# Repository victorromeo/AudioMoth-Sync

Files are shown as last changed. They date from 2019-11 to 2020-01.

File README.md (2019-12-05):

# AudioMoth-Sync

## DESCRIPTION

This project supports the Monash University AgTech Rodent Tracking project, to detect animal activity and trigger recording devices to acquire ultrasonic audio samples and photogrphic evidence required to document the animal activity and identify the related animal species.

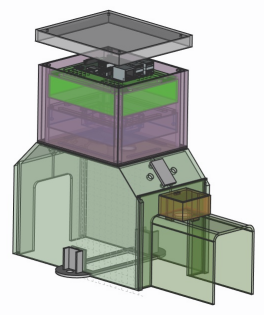
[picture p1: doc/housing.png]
Housing
<br>
*Original concept of the rodent detection housing*

## CONCEPT

An AudioMoth unit has a Cortex M4 EFM32WG380F256 MCU which is capable of supporting USB access as well as recording audio.
*(The two operations cannot occur at the same time however, as the processors internal capacity to handle the audio buffers and switch SD card access is insufficent)*

Instead, an AudioMoth is connected via USB to a Raspberry PI, and GPIO pins.  The Raspberry PI has PIR senses which detect the infrared emitted from animals.  

When an animal is detected, the Raspberry PI signals to the AudioMoth over GPIO to commence recording, and access to the AudioMoth sound recordings is removed.  In addition to the microphone activity, the Raspberry PI begins taking photos of animals inside the housing.  

When motion stops, after a delay the Raspberry PI signals to the AudioMoth to stop recording.  The AudioMoth enables the Mass Storage Device features on the MCU and the Raspberry PI detects the AudioMoth filesystem and mounts it.  Files are then transferred locally onto a microSD Card used by the Raspberry PI.  Once files are transferred, the recordings are removed from the AudioMoth microSD card, using remote access operations on the mounted filesystem.

A seperate background task, which is always running sends the sound and photo files into the cloud via a WiFi // 4G connection which is available.  Once the files are transmitted successfully to the cloud, the locally stored files are removed from the local device.

## PREREQUISITES

- Raspberry PI ([3B+](https://www.raspberrypi.org/products/raspberry-pi-3-model-b-plus/) or [4B](https://www.raspberrypi.org/products/raspberry-pi-4-model-b/))
    - 16GB or 32GB SD microSD card (For the OS)
    - [Raspbian](https://www.raspberrypi.org/downloads/raspbian/)
    - Power Supply
        - [2.5mA microUSB for RPi 3B+](https://www.raspberrypi.org/products/raspberry-pi-universal-power-supply/)
        - [15W Type-C for RPi 4B](https://www.raspberrypi.org/products/type-c-power-supply/)
        - Battery pack
        - 20W Solar panel and solar controller with load controller and external battery supply with USB support
        - PiJuice with LIPO battery and 20W Solar Panel
    - [RTC for Rpi](https://core-electronics.com.au/ds1307-rtc-module-with-battery-for-raspberry-pi.html)
    - [Duinotech XC9021 5MP Night Vision camera for Raspberry PI](https://www.jaycar.com.au/5mp-night-vision-camera-for-raspberry-pi/p/XC9021)
- AudioMoth (1.0.0 or later)
    - 16GB or 32GB SD microSD card (For the Audio samples)
    - [AudioMoth-MSD firmware](https://github.com/victorromeo/AudioMoth-MSD)
    - 2.54 right angle header 6 pin [female](https://core-electronics.com.au/0-100-2-54-mm-female-header-1x6-pin-right-angle.html) or [male](https://core-electronics.com.au/0-100-2-54-mm-breakaway-male-header-1x40-pin-right-angle.html)
    - [Dupont wires](https://www.altronics.com.au/p/p1017-prototyping-jumper-wires-mixed-for-breadboard-arduino/)
    - [Duinotech Raspberry Pi GPIO Expansion Shield](https://www.jaycar.com.au/duinotech-raspberry-pi-gpio-expansion-shield-with-4-x-ad-da/p/XC9050)
    - AA batteries to provide additional current requirements
- Housing
    - FreeCAD files
    - [Duinotech XC-4444 PIR Infrared Motion Sensor](https://core-electronics.com.au/modmypi-pir-infrared-motion-sensor-hc-sr501.html)
- Construction
    - Hot Glue gun
    - Soldering iron and Solder, used to mount the 6 pin header on the AudioMoth
    - 3D Printer (220 x 220 x 250 print bed), e.g. Ender 3
    - Silicon sealant

## RASPBERRY PI SETUP

### Setup of the Camera

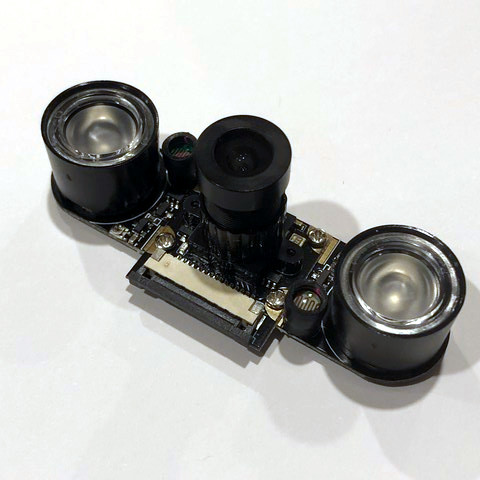
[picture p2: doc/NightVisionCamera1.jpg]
Camera


1. Run Raspi-Config to enable camera interface
    - `sudo raspi-config` ... `Interface Options` ... `Enable Camera` ... `Finish`
2. Power off the Raspberry PI
3. Plug in the 5 MP Nightvision camera
4. Power on the Raspberry PI
5. Execute `raspistill -o test.jpg` to validate that the camera is working, a file with the name test.jpg should appear in the current folder. If a screen is connected, view the image to validate that the photo is in focus.  If no screen is attached to the raspberry pi, use file transfer to view the image.

### Setup of the Realtime Clock

1. Run Raspi-Config to enable the I2C interface
    - `sudo raspi-config` ... `Interface Options` ... `Advanced Options` ... `I2C` .. `Finish`
2. Power off the Raspberry PI
3. Connect the RTC unit over pins 1-10 of the Raspberry PI
4. Power on the Raspberry PI
5. In a terminal window check to ensure the RTC chip is detected
    - `sudo i2cdetect -y 1` ... 68, which is the RTC hexidecimal I2C address of the device should appear
6. Load the RTC module
    - `sudo modprobe rtc-ds1307`
7. Register the device
    - `sudo echo ds1307 0x68 > /sys/class/i2c-adapter/i2c-1/new_device`
8. Read the time from the RTC
    - `sudo hwclock -r`
9. If the Raspberry PI device is connected to the internet via WiFi or Ethernet, check the time
    - `date`
10. Write the time to the RTC
    - `sudo hwclock -w`
11. Add the RTC clock to the Raspberry PI modules list
    - `sudo nano /etc/modules` and add `rtc-ds1307` at the end of the file. Save (Control + o) and exit (Control + x, y).
12. Add the RTC clock to the boot script
    - `sudo nano /etc/rc.local` and add the following.

    ```
    echo ds1307 0x68 > /sys/class/i2c-adapter/i2c-1/new_device
    sudo hwclock -s
    date
    ```
    Save (Control + o) and exit (Control + x, y).
13. Disconnect the network and check that time is still accessible
    - `date`

### Setup Python 3

1. Update the list of available packages
    - `sudo apt update`
2. Upgrade the currently installed packages
    - `sudo apt upgrade`
3. Install the picamera component
    - `sudo apt install python3-picamera`

### Setup Sync Scripts

1. Change to home directory of
    - `cd ~`
2. Clone the scripts into the root directory
    - `git clone https://github.com/victorromeo/AudioMoth-Sync.git`

### Setup Cron Job

1. Change to the directory of the AudioMoth-Sync
    - `cd ~/AudioMoth-Sync`
2. Update exec permission on the launcher script
    - `chmod 755 launcher.sh`
3. Test that the script executes
    - `sh launcher.sh`
4. Add launcher.sh to crontab
    - `sudo crontab -e` and add the following to the end of the file
    - `@reboot sh /home/pi/AudioMoth-Sync/launcher.sh > /home/pi/AudioMoth-Sync/logs/cronlog 2>&1`
5. Power off the Raspberry PI
6. Power on the Raspberry PI
7. Troubleshoot by inspecting the logs
    - `cat /home/pi/AudioMoth-Sync/logs/cronlog`

## AUDIOMOTH SETUP

### Flash the firmware

1. Download the firmware from AudioMoth-MSD
2. Connect the AudioMoth to a PC a USB cable
3. [Flash](https://github.com/OpenAcousticDevices/Flash) the device, using the AudioMoth-Project.bin file and instructions on the flash project.  Briefly this can be explained as follows
    - Connect pins 1 and 3 together, (pulling the SWCLK to VCC)
    - Change the switch to the Custom setting on the AudioMoth
    - `flash -i /dev/ttyACM0` or similar, to get the serial number
    - `flash -u /dev/ttyACM0 AudioMoth-Project.bin` (execute several times as needed to get the firmware to upload onto the device)

### Connectors

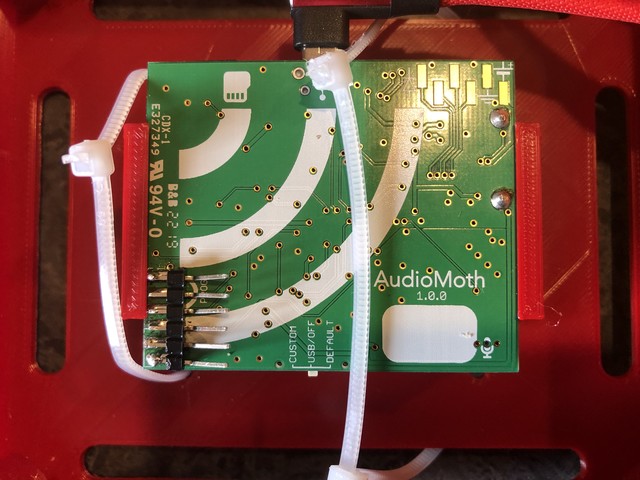
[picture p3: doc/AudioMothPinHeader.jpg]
AudioMoth Headers


1. Solder the 2.54 right angle header 6 pins onto the AudioMoth
2. Connect Dupont connectors onto the pins, exposing female connectors on the opposite end available to connect onto the Raspberry PI

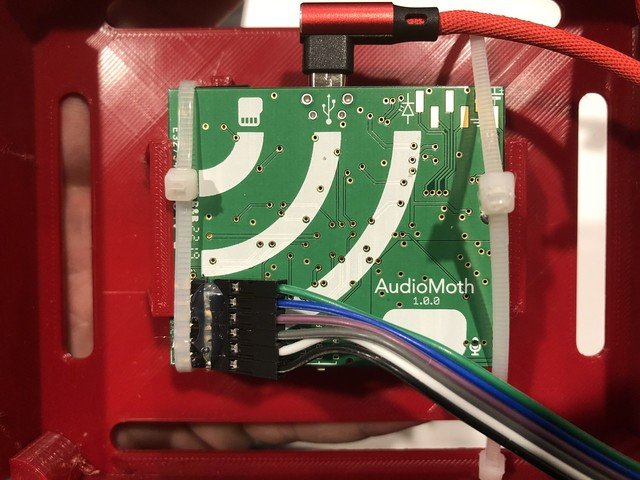
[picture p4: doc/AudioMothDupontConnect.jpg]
AudioMoth Header Connections


## CONSTRUCTION

### 3D Print the housing 

You will require
- 1 x Lid
- 1 x Electronics Unit
- 1 x Electronics Base
- 1 x AudioMoth Holder
- 1 x Raspberry PI Holder
- 2 x Trap Sides
- 2 x Trap Brackets
- 2 x Tunnels
- 2 x PIR Cover
- 1 x Peg Bracket

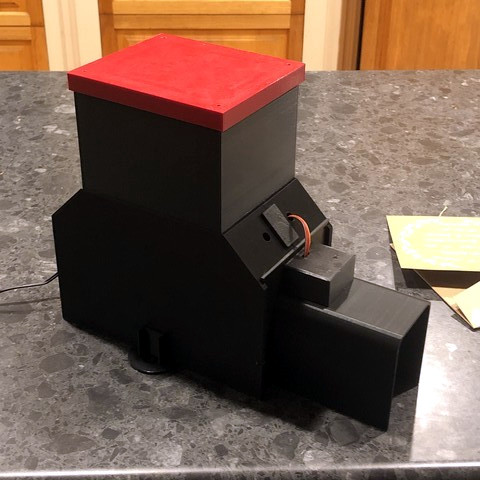
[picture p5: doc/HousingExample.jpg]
Housing Example
<br>
*Housing*

### PIR Installation

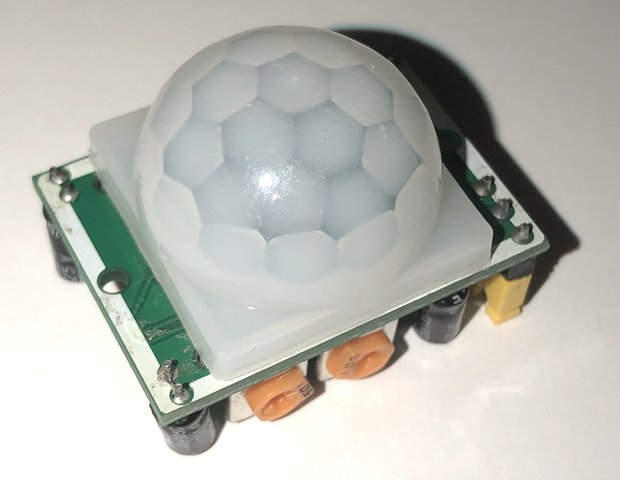
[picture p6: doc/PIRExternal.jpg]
PIR


1. Sit the PIR unit in the hole in top of the Tunnel, white dome facing downward, and secure with Hot Glue to prevent movement.

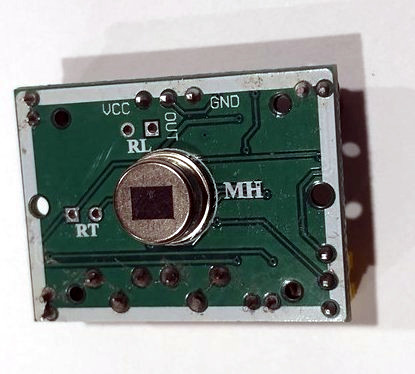
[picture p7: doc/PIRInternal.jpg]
PIR Internal


2. Connect Dupont cables to the 3 header pins point upward.
The pins are VCC (5 Volt), OUT (3.3V Max), GND

3. Tune the PIR sensitivity as required.  Default settings should be adequate. 

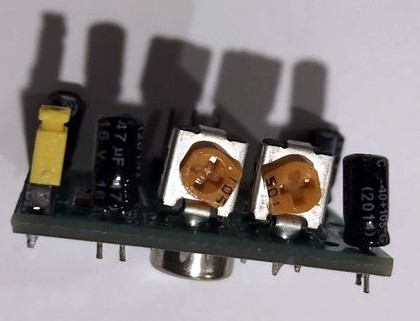
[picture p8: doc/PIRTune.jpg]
PIR Tune


### Wiring GPIO 

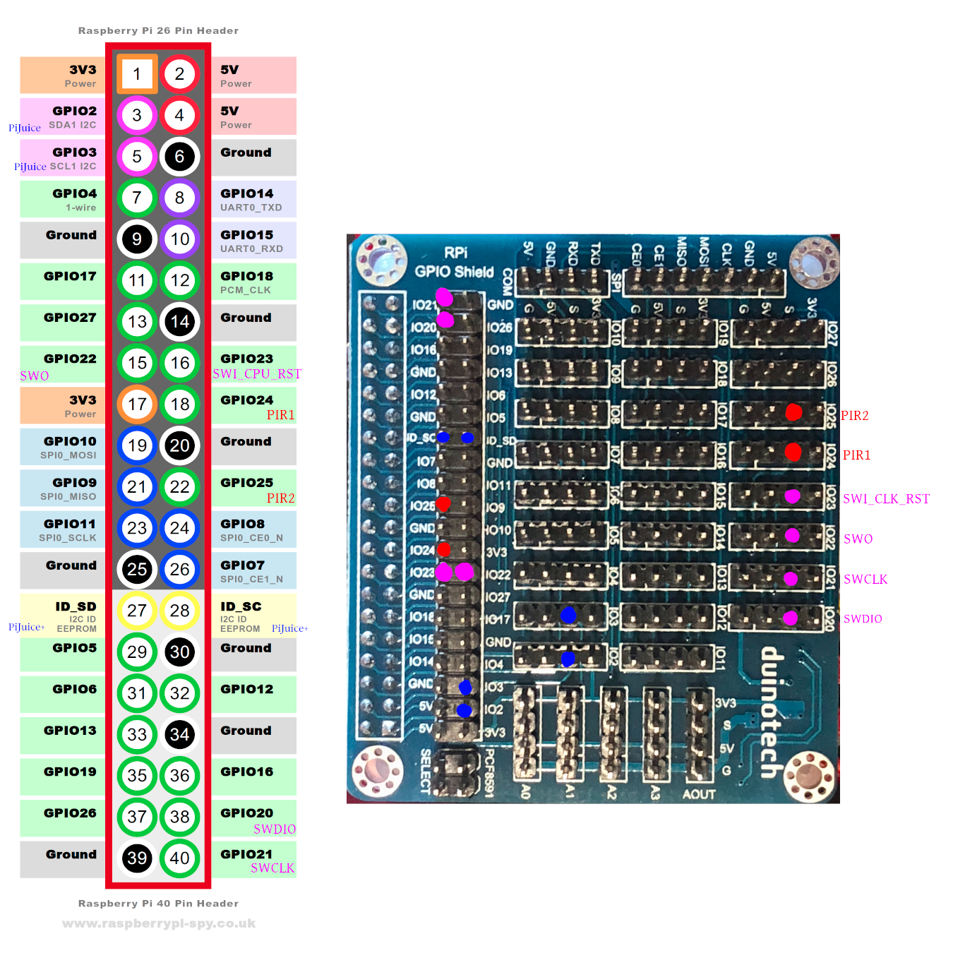
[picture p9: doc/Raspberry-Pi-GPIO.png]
AudioMoth Pins
<br>
*GPIO Expansion Header*

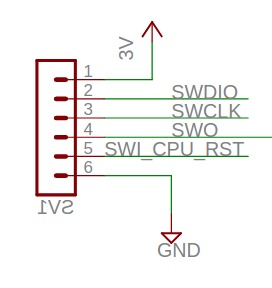
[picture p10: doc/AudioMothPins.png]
GPIO Connections
<br>
*AudioMoth Pins - On AudioMoth 1.x.0 pin closest to the corner is Ground*

| Function                                   | Source          | RPi Header Pin Number | Raspberry PI GPIO ID |
| ------------------------------------------ | ----------------| --------------------- | -------------------- |
| AudioMoth SWDIO                            | AudioMoth Pin 2 | 38                    | IO20                 |
| AudioMoth SWCLK                            | AudioMoth Pin 3 | 40                    | IO21                 |
| AudioMoth SWO                              | AudioMoth Pin 4 | 15                    | IO22                 |
| AudioMoth SWI_CPU_RST                      | AudioMoth Pin 5 | 16                    | IO23                 |
| PIR 1 Motion (5V and GND pins needed also) | PIR 1 Out       | 18                    | IO24                 |
| PIR 2 Motion (5V and GND pins needed also) | PIR 2 Out       | 22                    | IO25                 | 

### PiJuice

```text
PiJuice GPIO Pin Allocations (Taken from PiJuice documentation)
-----------------------------------------------------------------------------------------------------------------------
| 2     4     6     8    10    12    14    16    18    20    22    24    26    28    30    32    34    36    38    40 |
|5V    5V    GND   o     o     o     GND   o     o     GND   o     o     o     +     GND   o     GND   o     o     o  |
|3V3   #     #     o     GND   o     o     o     3V3   o     o     o     GND   +     o     o     o     o     o     GND|
| 1     3     5     7     9    11    13    15    17    19    21    23    25    27    29    31    33    35    37    39 |
-----------------------------------------------------------------------------------------------------------------------

# Used
o Available
+ Can be reused

3 I2C_SDA to MCU
5 I2C_SCL to MCU
27 I2C_SDA to HAT EEPROM
28 I2C_SDL to HAT EEPROM
```

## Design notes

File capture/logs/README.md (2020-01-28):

# AudioMoth-Sync

## logs

**All records are in UTC time**

This folder is reserved for the destination of log files generated while processing the python scripts in the parent folder. The logs will be synchronised into the cloud, and deleted daily, via a cron job.

### system-[%Y%m%d]-.log
(daily log file)

The System log is for background tasks which manage the operating system
- job_check_power    Gets details of the current power supply and battery
- job_cleanup        Removes old files
- job_git_pull       Gets the latest AudioMoth-Sync
- job_launch         Starts AudioMoth-Sync
- job_network_switch Switches Wifi networks if offline by highest wpa_supplicant priority
- job_reverse_ssh    Establishes a SSH reverse tunnel to the main agtech server
- job_send_heartbeat Sends a message to the agtech server regularly to notify of connectivity
- job_startup        Called when the host device starts up @reboot
- job_stop           Called to stop the AudioMoth-Sync, setting a config.ini flag
- job_sync_aws       Sends the current audio, photo, video and log data to S3, then pulls latest binary files and AudioMoth firmware

All records should follow the following pattern:

%Y%m%d-%H%m%s $HOSTNAME "alias" /path/to/script.sh

### activity-[%Y%m%d].log

The activity log is for internal operations done within the AudioMoth-Sync application

%Y%m%d-%H%m%s $HOSTNAME "operation" "action" "result"

### event.log

An incremental logfile to record all detection events.
Useful to correlate logs, audio, photos and video files

$EVENT_ID %Y-%m-%dT%H:%m:%s.%fffff:%zzzz $HOSTNAME

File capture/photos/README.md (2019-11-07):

# AudioMoth-Sync
## visual

This folder is reserved for the destination of photographs, acquired from the camera and yet to be synchronised into the cloud.

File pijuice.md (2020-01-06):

# PIJUICE configuration

PiJuice pins

## Prerequisite steps

1. Power down the Raspberry PI
2. Connect the PiJuice hat onto the Raspberry PI
3. Connect the battery, replacing the supplied low capacity battery
4. Connect the power supply to the PiJuice power port
5. Start the Raspberry PI by pressing the SW1 button, closest to the power port

## Setup the RTC clock

Running `i2cdetect -y 1` from bash will give the following result.  Note where `UU` appears, which in this case below is at `0x68`.

```bash
pi@rpi-stretch-full:~ $ i2cdetect -y 1
     0  1  2  3  4  5  6  7  8  9  a  b  c  d  e  f
00:          -- -- -- -- -- -- -- -- -- -- -- -- --
10: -- -- -- -- 14 -- -- -- -- -- -- -- -- -- -- --
20: -- -- -- -- -- -- -- -- -- -- -- -- -- -- -- --
30: -- -- -- -- -- -- -- -- -- -- -- -- -- -- -- --
40: -- -- -- -- -- -- -- -- -- -- -- -- -- -- -- --
50: -- -- -- -- -- -- -- -- -- -- -- -- -- -- -- --
60: -- -- -- -- -- -- -- -- UU -- -- -- -- -- -- --
70: -- -- -- -- -- -- -- --                         
pi@rpi-stretch-full:~ $
```

1. To manually set the RTC clock, run `sudo date -s '2020-01-05 12:01:34` then `sudo hwclock -w` to write the time to the RTC chip
2. Add a line `sudo hwclock -s` into the `/etc/rc.local` file, to copy the RTC time back to the system clock at boot.

## Installation

1. First install the command line

  ```bash
  sudo apt-get install pijuice-base
  ```

1. Then install the GUI

   ```bash
   sudo apt-get install pijuice-gui
   ```

## PIR Alteration

The PIR requires a circuit modification to support a 3V3 supply voltage, instead of the onboard voltage regulator.

PIR Rewire

1. Remove the 7133-1 chip, by adding solder to the 4 terminals (1 above and 3 below)
2. remove the diode, again by adding solder to the terminals
3. add an insulated jumper wire between the location of the now removed voltage regulator and diode, (wire shown in green)
4. Remove the header jumper
5. Tune the PIR
6. Connect the PIR to the PiJuice

PIR Connect

## Configuration

1. Start a bash terminal
2. Run `pijuice_cli`
3. Select the `System Task` menu page
   1. Select `System task enabled` checkbox
   2. Select the `Software Halt Power Off` Delay period (30 seconds)
   3. Select `Apply Settings`
   4. Select `Back` to return to the main menu
4. Open the `Battery Settings` page
   1. Select the `PJLIPO_12000` battery profile
   2. Using the down direction arrow on your keyboard, scroll down
   3. Select `Apply settings`
   4. Select `Back` to return to the main menu
5. Open the `IO Settings` page
    1. Select `IO2`
    2. Select `Mode: DIGITAL_IN`
    3. Select `Pull: PULLDOWN`
    4. Select `Wakeup: RISING_EDGE`
    5. Select `Apply`
    6. Select `Back` then `Back` again to return to the main menu
6. Select `Wakeup Alarm` page
   1. Select `Wakeup enabled` checkbox
   2. Select `Day`, `Every Day` and `Every Hour`
   3. Select `Minutes Period`
   4. Set Minute to 30 (Configurable)
   5. Select `Set Alarm`
   6. Select `Back` to return to the main menu

## Wake-up configuration

The following script (which is part of the project code already), ensures that following a wake up, the raspberry pi device is configured to allow future wake ups by alarm.

```bash
#!/usr/bin/python3
# This script is started at reboot by cron
# Since the start is very early in the boot sequence we wait for the i2c-1 device

import pijuice, time

while not os.path.exists('/dev/i2c-1'):
    time.sleep(0.1)

pj = pijuice.PiJuice(1, 0x14)

pj.rtcAlarm.SetWakeupEnabled(True)

```

run `sudo crontab -e`

add the following record

`@reboot /usr/bin/python3 /home/pi/Documents/AudioMoth-Sync/pijuiceWakeupEnable.py`

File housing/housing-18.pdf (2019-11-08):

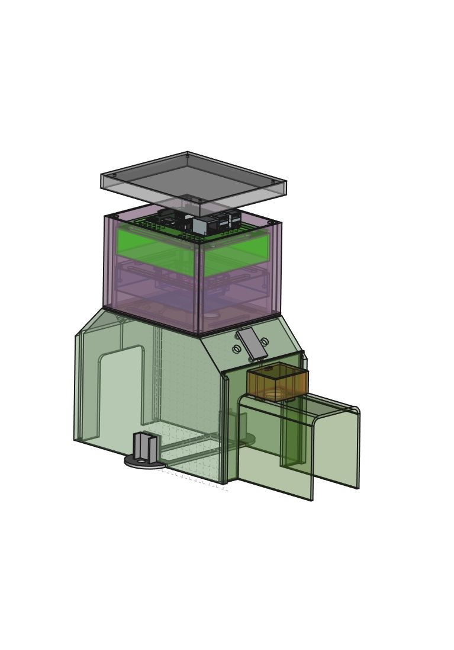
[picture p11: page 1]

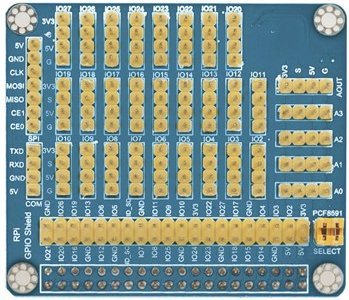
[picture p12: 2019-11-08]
doc/XC9050.jpg

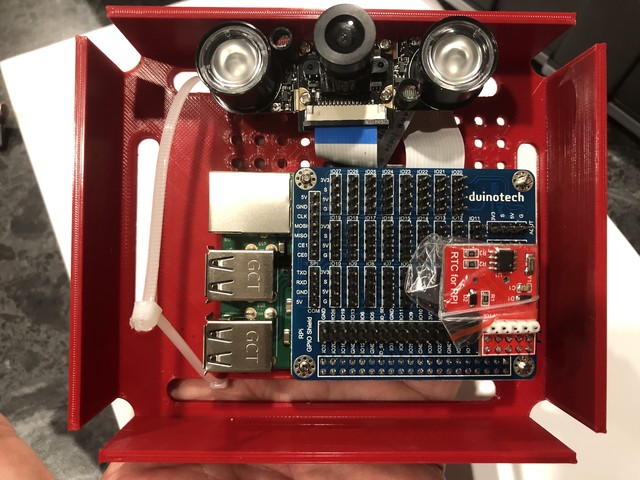
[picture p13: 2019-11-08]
doc/RaspberryPiGPIO.jpg

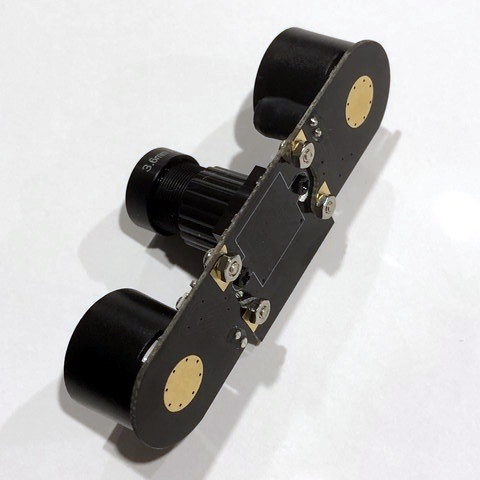
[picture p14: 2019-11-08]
doc/NightVisionCamera2.jpg

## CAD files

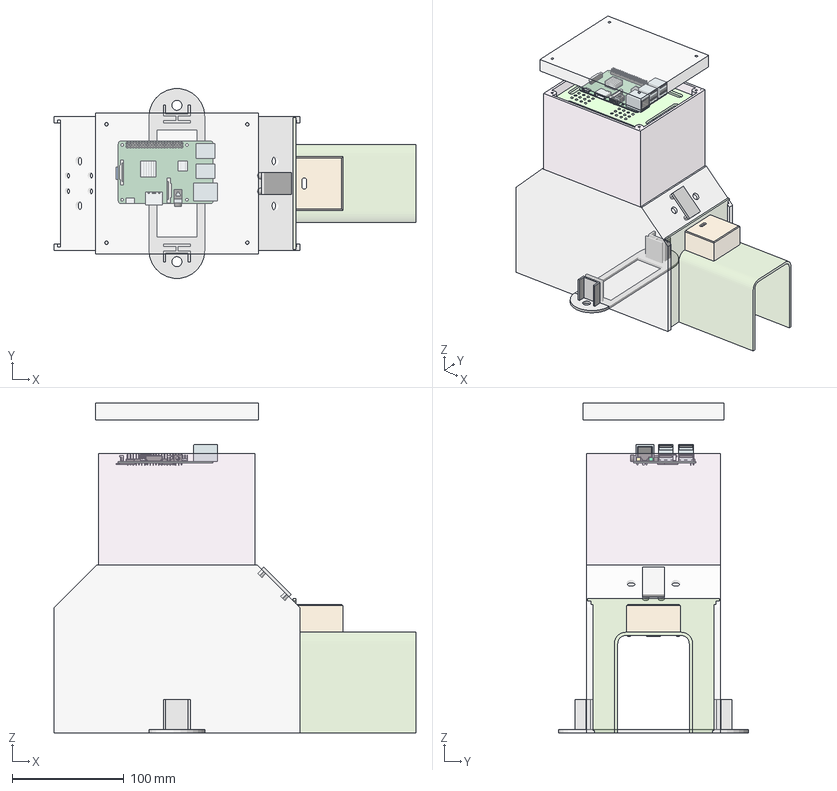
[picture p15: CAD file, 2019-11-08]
housing/housing-18.FCStd
324.0 x 169.6 x 295.0 mm
Trap
Electronics
Tunnel
Lid
ElectronicsBase
AudioMoth
Raspberry Pi 3
Raspberry Pi 004
Raspberry Pi 005
Raspberry Pi 006
Raspberry Pi 007
Raspberry Pi 008
Raspberry Pi 009
Raspberry Pi 010
Raspberry Pi 011
Raspberry Pi 012
Raspberry Pi 013
Raspberry Pi 014
Raspberry Pi 015
Raspberry Pi 016
Raspberry Pi 017
Raspberry Pi 018
Raspberry Pi 019
Raspberry Pi 020
Raspberry Pi 021
Raspberry Pi 022
Raspberry Pi 023
Raspberry Pi 024
Raspberry Pi 025
Raspberry Pi 026
Raspberry Pi 027
Raspberry Pi 028
Raspberry Pi 029
Raspberry Pi 030
Raspberry Pi 031
Raspberry Pi 032
Raspberry Pi 033
Raspberry Pi 034
Raspberry Pi 035
Raspberry Pi 036
Raspberry Pi 037
Raspberry Pi 038
Raspberry Pi 039
Raspberry Pi 040
Raspberry Pi 041
Raspberry Pi 042
Raspberry Pi 043
Raspberry Pi 044
Raspberry Pi 045
Raspberry Pi 046
Raspberry Pi 047
Raspberry Pi 3 (micro SD)
Raspberry Pi 048
RPi Heatsink Set
RPi Heatsink Set001
Shapes
Raspberry Pi 049
Shapes001
Shapes002
Shapes003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

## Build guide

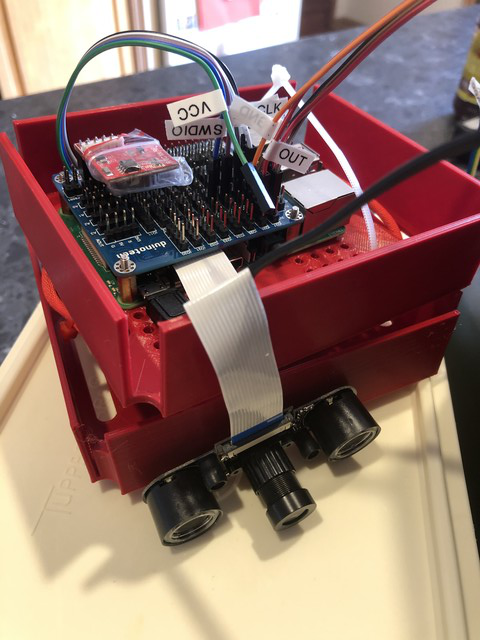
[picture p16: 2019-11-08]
doc/PreInstallation3.jpg

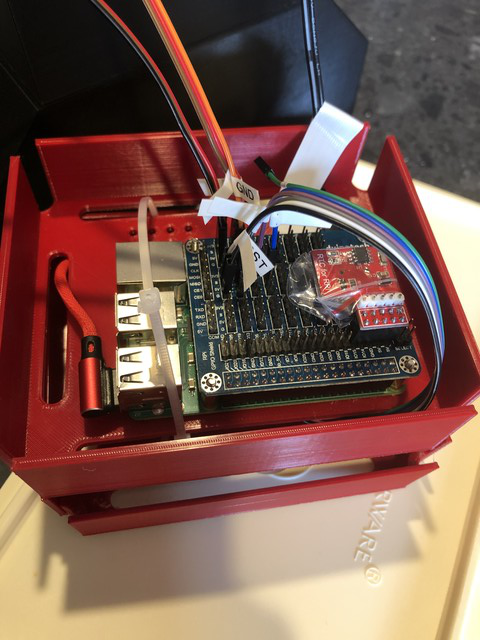
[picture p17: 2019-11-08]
doc/PreInstallation1.jpg

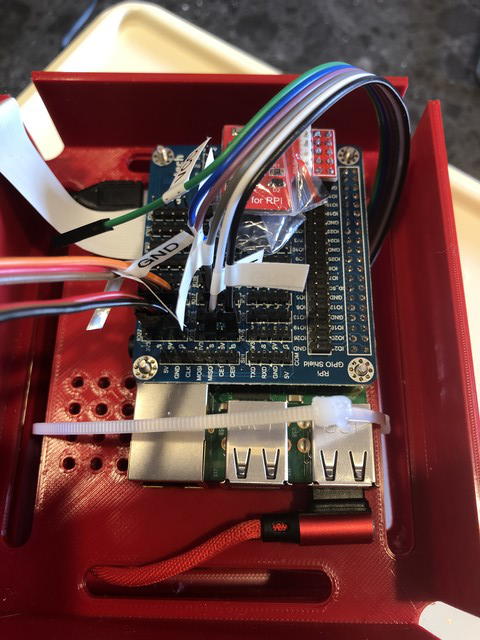
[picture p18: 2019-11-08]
doc/PreInstallation2.jpg

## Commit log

2019-11-08 Added FreeCAD housing
    [housing-18.FCStd]
2019-12-05 Update with PiJuice and GPIO pin changes
2019-12-06 Separated motion sensor
2019-12-06 Separated camera
2020-01-15 Added pwr pin to detect Moth
2020-01-17 Fixed device name population
2020-01-21 Added Check Power to log battery issues
2020-01-22 Fixed tests and AM mount
2020-01-22 Fix power check freq
2020-01-26 Fixed device name compatibility
2020-01-30 power monitoring for sleeping
